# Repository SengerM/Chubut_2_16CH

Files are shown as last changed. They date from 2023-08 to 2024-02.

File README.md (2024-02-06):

# Chubut 2 16 channels

This repository contains source files of the *Chubut 2 16 channel readout board*. This board was designed to facilitate multi-channel readout of LGAD silicon sensors, such as TI-LGAD, AC-LGAD, etc. More information in [this link](https://sengerm.github.io/Chubut_2_16CH/doc/230810_characterization/main.html).

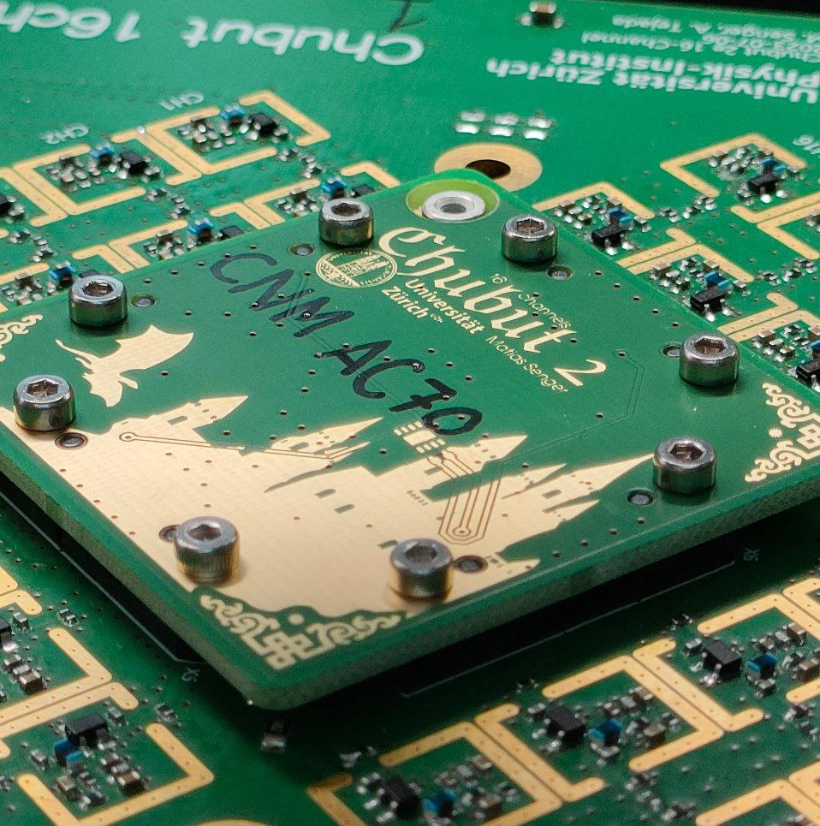
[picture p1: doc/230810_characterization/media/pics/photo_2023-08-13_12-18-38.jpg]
Picture of the Chubut 2 16ch board


Time resolution measured with a 90Sr source

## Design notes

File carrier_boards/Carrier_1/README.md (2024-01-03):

# Carrier 1

This is a general purpose carrier board for the Chubut 2 16ch readout board and can host sensors up to 3×3 mm².

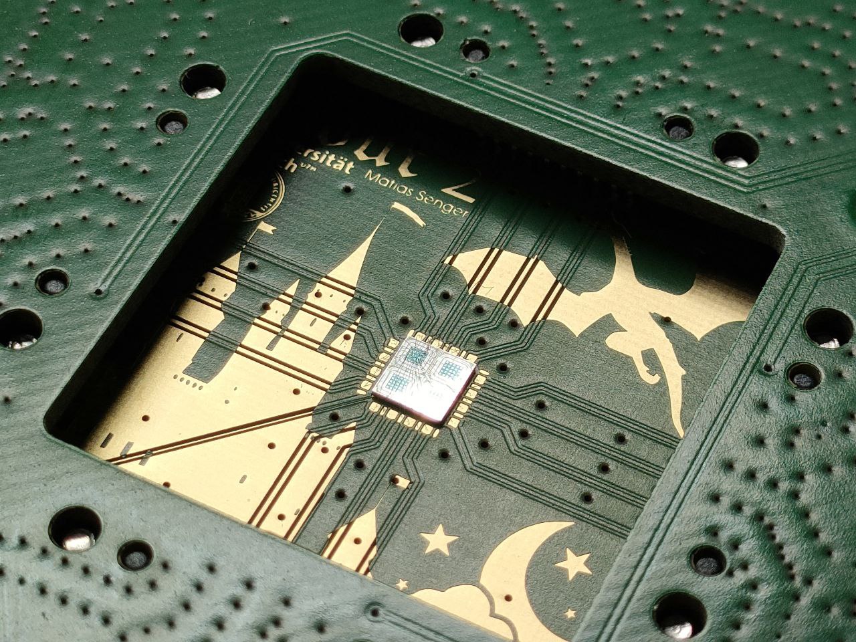
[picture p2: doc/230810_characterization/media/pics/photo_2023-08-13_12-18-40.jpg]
A picture of the Carrier 1 board


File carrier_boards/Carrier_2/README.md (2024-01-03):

# Carrier 2

This carrier board was specifically designed to host AC-LGADs manufactured by FBK, which are usually diced in groups of 3 and do not fit in other boards.

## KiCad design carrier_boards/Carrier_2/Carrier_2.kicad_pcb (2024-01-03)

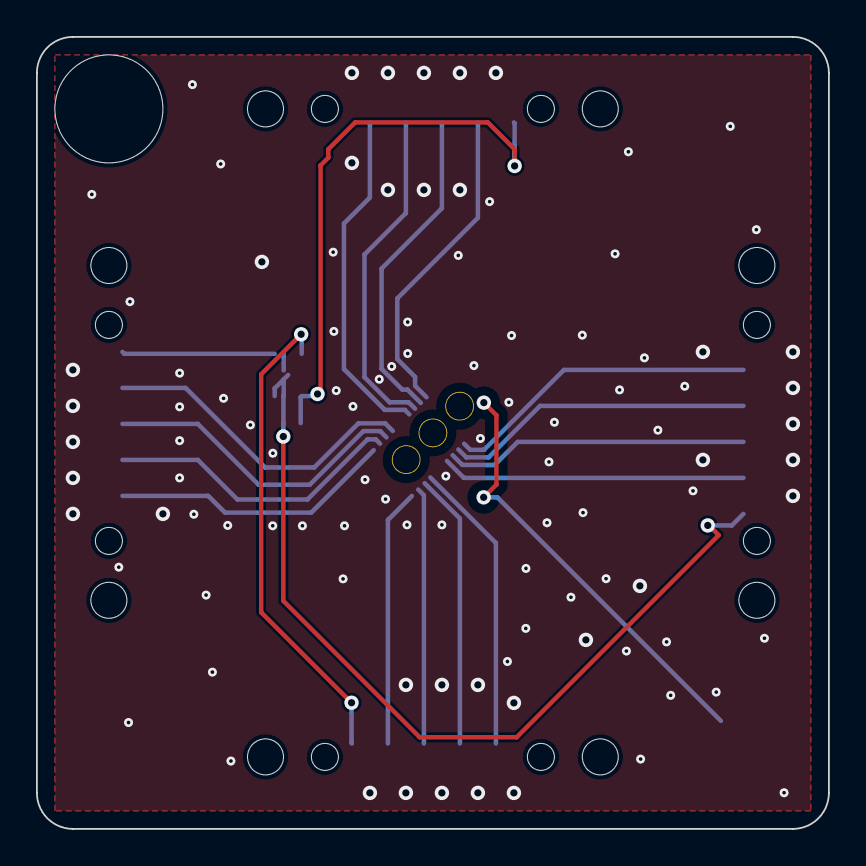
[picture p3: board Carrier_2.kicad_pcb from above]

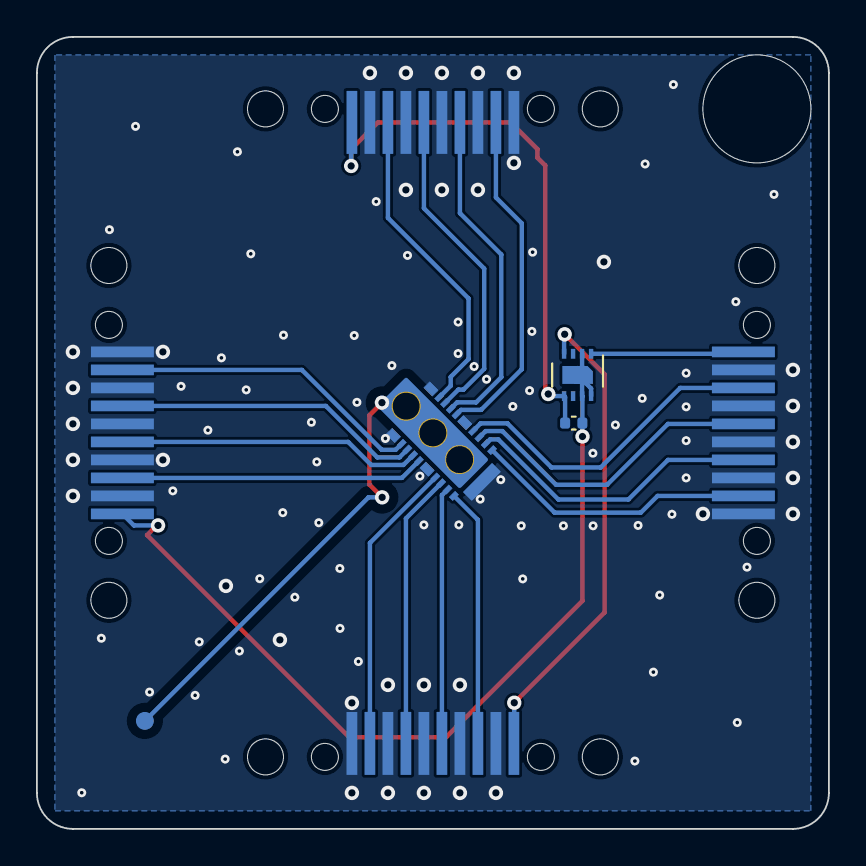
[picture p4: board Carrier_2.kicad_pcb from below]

Board: 2 copper layers, 44.0 x 44.0 mm, 9 parts (8 on the bottom side), 22 nets.

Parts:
C1: 100n; C_0402_1005Metric
H1: MountingHole; alignment_hole
J5: HV; pogo_pin_mating_pad
U1: FBK_RSD2_3_DUTs_together
U2: SHT30-DIS; Sensirion_DFN-8-1EP_2.5x2.5mm_P0.5mm_EP1.1x1.7mm
X4, X5, X6, X7: FSI-110-03-G-S-M-AD

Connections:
/HV: J5.1, U1.17 (HV)
/I2C_GND: C1.2, U2.2 (ADDR), U2.7 (R), U2.8 (VSS), U2.9 (VSS), X6.10
/I2C_POWER: C1.1, U2.5 (VDD), X7.10
/SCL: U2.4 (SCL), X5.10
/SDA: U2.1 (SDA), X4.10
GND: U1.18 (GND), X4.1, X4.3, X4.5, X4.7, X4.9, X5.1, X5.3, X5.5, X5.7, X5.9, X6.1, X6.3, X6.5, X6.7, X6.9, X7.1, X7.3, X7.5, X7.7, X7.9
unnamed: U1.1 (0,0), X4.2
unnamed: U1.15 (0,1), X5.6
unnamed: U1.14 (0,2), X5.4
unnamed: U1.12 (0,3), X6.8
unnamed: U1.2 (1,0), X4.4
unnamed: U1.16 (1,1), X5.8
unnamed: U1.13 (1,2), X5.2
unnamed: U1.11 (1,3), X6.6
unnamed: U1.3 (2,0), X4.6
unnamed: U1.5 (2,1), X7.2
unnamed: U1.7 (2,2), X7.6
unnamed: U1.10 (2,3), X6.4
unnamed: U1.4 (3,0), X4.8
unnamed: U1.6 (3,1), X7.4
unnamed: U1.8 (3,2), X7.8
unnamed: U1.9 (3,3), X6.2

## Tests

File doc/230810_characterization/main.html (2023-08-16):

Matías Senger

August 2023

This document presents the Chubut 2 16ch board, which is a version of the Chubut 2 board (https://github.com/SengerM/Chubut_2) but with 16 channels instead of 4. The board is introduced, as well as a characterization using a radioactive beta source.

## Contents

# Introduction

The Chubut 2 16ch readout board is a readout board designed for testing LGAD devices. It has 16 independent channels with built in amplification for each channel. The circuitry for each channel is replicated from the original Chubut 2 . Each channel has 2 amplification stages, making it possible to measure LGADs without the need for external amplifiers. A scheme of the board is shown in . It consists of two boards, one is the main board which contains the electronics, shown in the left of , and the other is the carrier board which only hosts the DUT, shown in the right of . The advantage of this design with a main and a carrier board is that the main board can be utilized multiple times to measure different DUTs, reducing monetary cost and work load. The carrier board fits only in one position, so it is not possible to install it wrong, and is held in place using screws. This can be seen in the pictures sown in .

 Schematic diagram of the Chubut 2 16ch readout board.

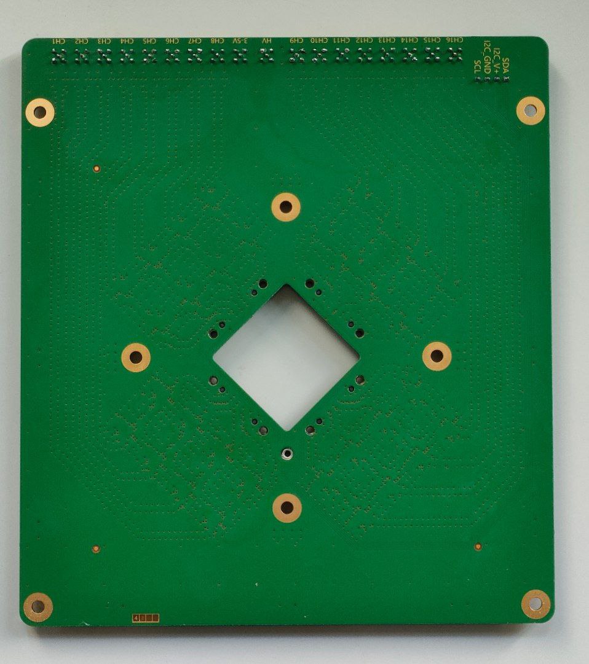
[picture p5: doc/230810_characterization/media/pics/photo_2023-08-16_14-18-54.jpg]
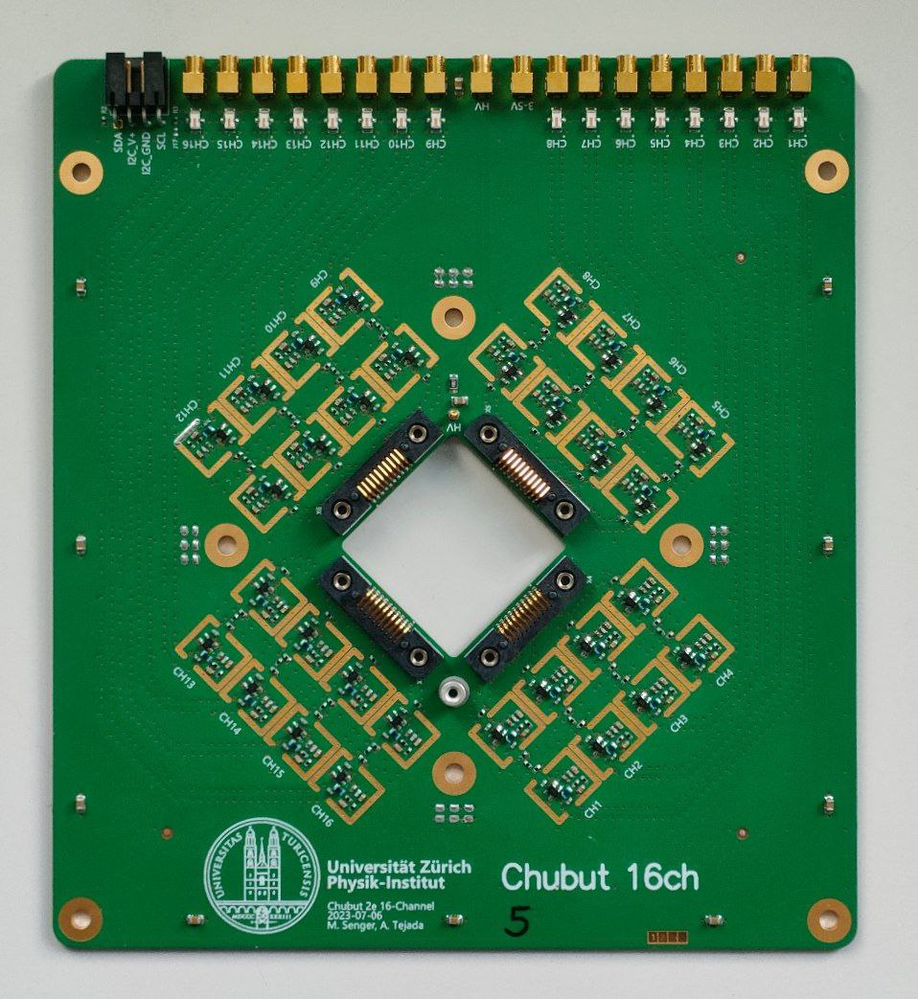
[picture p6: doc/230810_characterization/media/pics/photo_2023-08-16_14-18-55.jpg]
   

Pictures of the Chubut 2 16ch readout board.

In the following sections, more details of the board are presented.

# Temperature raise

Due to the Chubut 2 16ch readout board having 16 channels, each with two amplification stages, a considerable amount of power is dissipated. When operated at 3 V the total current drained is 700-800 mA, which means a total power of 2-2.5 W. Close to the area where the amplifiers are located, there is power dissipation and thus the temperature increases. In order to examine how much the temperature increases, pictures with a thermal camera were taken. These pictures are shown in . When these pictures were taken, the board was installed in our TCT setup. The ambient temperature, as seen in the photos, was 20 ℃. The area close to the amplifiers was approximately 12.5 ℃ higher, while the carrier board where the DUT was mounted is approximately at 27 ℃, i.e. 5 ℃ higher than ambient temperature. The carrier board is designed with the possibility of hosting a Sensirion SHT31-DIS-B (https://sensirion.com/products/catalog/SHT31-DIS-F) temperature and humidity sensor, so the temperature can be monitored.

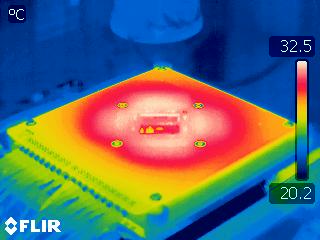
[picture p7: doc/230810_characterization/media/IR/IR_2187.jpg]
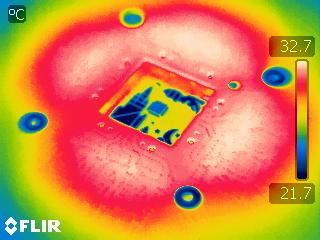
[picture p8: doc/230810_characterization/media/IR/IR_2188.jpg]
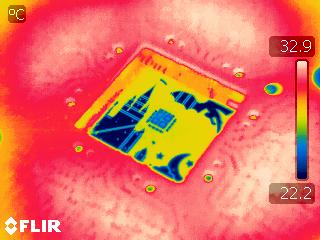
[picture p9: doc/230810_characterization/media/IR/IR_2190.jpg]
  

Photographs of the Chubut 2 16ch readout board during operation taken with a thermal camera.

# Characterization with beta source

To characterize the readout board, a TI-LGAD was mounted and exposed to radiation from a ⁹⁰Sr beta source. In a schematic representation of the measuring setup is shown. The TI-LGAD used is from the RD50 FBK production, wafer 16, 2 trenches, pixel border V2 and contact type ring. This device has a 4×4 layout with a pitch of 250 µm. The 16 pixels from the DUT were connected to each output of the readout board. The measurement was performed at +20 ℃, because the board is intended to be used in the test beam setup, probably at room temperature. The signals from the outputs of the readout board, as well as the trigger signal from the MCP-PMT, were digitized using a CAEN DT5742 digitizer, as shown in the diagram.

 Diagram of the arrangement and connections for the beta source testing.

The first check was to verify the integrity of the digitized waveforms. In example waveforms from a random event are shown. The first plot shows the raw data as provided by the digitizer. We see that channel 2 (signal_name DUT_2) has a negative peak, consistent with the expected polarity given the type of DUT, and the two channels called MCP_PMT_1 and MCP_PMT_2 have a positive peak, consistent with the expected polarity for the MCP-PMT followed by an inverting amplifying stage. The reason there are two waveforms corresponding to the MCP-PMT is due to technical details regarding the implementation of the digitizer; the 16 channels are split in two groups of 8 channels each, and each of these groups has an independent trigger signal which comes from an internal splitting of the TR0 input . For the channel 2 (DUT_2), which is the one that was hit by the beta particle in this example event, the corresponding MCP_PMT_1 is the correct trigger signal to use when calculating time quantities. In the same figure (, scroll to the right), two additional plots are shown with details of how each of the two relevant waveforms from this example are processed by the analysis algorithms. By zooming in, it can be seen that the analysis software performs a linear interpolation of the waveforms.

Waveforms from a particular event, as an example. In the first plot, the raw data from the digitizer is shown. The second and third plot (scroll horizontally) show how the relevant waveforms from the DUT and the MCP-PMT were processed.

Similar waveforms as the ones shown in are observed for all the channels. To get a first impression of how things work, it is useful to produce for all the individual waveforms a scatter plot in which the x axis is the time of the peak as measured from the trigger and the y axis is the amplitude of the signal. Such plot is shown in for a subset of the eventsThe reason for showing only a random subset of events is because otherwise the number of points in the plot is overwhelming and it becomes too heavy to load., without applying any filter. The x axis shows the quantity t_50 - t_50_trigger which is a measure of the peak time with respect to the trigger time. The quantity t_50 is the time at which the peak goes over its 50 %, as shown in the two right plots of , while t_50_trigger is the same quantity but for the corresponding MCP_PMT_1 or MCP_PMT_2 depending on the trigger group at which the channel belongs to, as described previously. In this figure we see that the majority of events distribute randomly in time and with amplitudes of approximately ±2 mV (zoom in vertically to see), which corresponds to waveforms without signal from a beta particle. There is another component in this distribution for which the time (x axis) is well localized, between ±1 ns (zoom in horizontally to see better) and negative amplitudes ranging from -40 mV and larger. These points represent the signals in each pixel of the DUT. The points corresponding to the two signals of the MCP-PMT are all perfectly aligned at t=0, the reason is that these signals are themselves the triggers, so the time with respect to the trigger is, by definition, 0.

Scatter plot of waveform amplitude vs time from trigger defined as the time from the waveform crossing the 50 % and the trigger crossing the 50 %.

To proceed further with the analysis, a threshold in the amplitude is imposed to all the DUT signals to select only those events in which the channels have an amplitude of 40 mV or larger in absolute value. In this way, all the empty waveforms are removed. shows the distribution of amplitudes after performing the selection of events. The plot on the left shows the empirical cumulative distribution function (ECDF) and the plot on the right (scroll horizontally) shows a histogram and a langauss fit (Landau convoluted with Gaussian) to each channel. In this last plot, the traces can be enabled for the channels not shown by clicking on the elements in the legend, only channels 1 and 2 are shown by default for the sake of clarity.

Amplitude distribution after selecting those waveforms with an amplitude larger than 40 mV in absolute value. In these plots, the quantity shown is the amplitude multiplied by -1 to make it positive. The first plot shows the empirical cumulative distribution function (ECDF) and the second plot shows the histograms together with a langauss fit (Landau convoluted with a Gaussian). To enable/disable traces, click on the elements in the legend.

In the distribution for other parameters, after applying the cuts in the amplitude, are shown (scroll horizontally if needed to see all of them). As seen, the signal to noise ratio has a median that oscillates between 120 and 135, for the rise time the median oscillates between 980 and 1010 ps, the median noise is between 610 and 660 µV, the median pulse duration above 50 % threshold is between 1.42 and 1.48 ns and the integral under the peak, called Collected charge (V s) in the plot, has a median between 115 and 138 ×10⁻¹² V s. All these quantities are calculated individually for each waveform as shown in the two example plots to the right in . From all these distributions, and the ones shown in , it can be concluded that the system is performing properly and the response of each channel is uniform.

Other distributions obtained in the same conditions as for the ones shown in , i.e. after selecting the events by amplitude. The quantities shown in these plots correspond to the parameters shown in the analyzed waveforms to the right in . Scroll horizontally to see all of them.

Among the most important parameters to be determined using the readout board is the time resolution of the DUT. To calculate the time resolution, or, firstly, the jitterHere, jitter is understood as the fluctuations in the time at which a signal crosses some threshold, see this image (https://upload.wikimedia.org/wikipedia/commons/thumb/8/8d/Jitter_timing.svg/660px-Jitter_timing.svg.png) taken from the Wikipeida article on jitter (https://de.wikipedia.org/wiki/Jitter)., the time information from each peak is extracted. This information conists on a set of 9 parameters extracted from each peak, labeled t_10, t_20, ..., t_90 that measure the time at which the peak went above the corresponding percentage of its own amplitude, i.e. applying a constant fraction discrimination, as shown in the two plots on the right in . Having these values, then it is possible to select any pair of signals, say DUT_1 and MCP_PMT_1, and calculate the time difference for some pair of kCFD values, say 20 % and 20 %. This means to compute Δt = t_20DUT_1 - t_20MCP_PMT_1 for each event. An example is shown in . The fluctuations observed in Δt correspond to the jitter for this particular choice of signals and thresholds, i.e. the fluctuation in the time for which one of the signals crosses some threshold, regarding the other as the time reference.

Example of Δt distribution for kCFD, DUT_4=40 % and kCFD, MCP_PMT_1=50 %, together with a Gaussan fit.

The pairs of signals for which the jitter is relevant are each of the DUT channels and the corresponding trigger signal according to the trigger group, as detailed previously, which is coming from the MCP-PMT time reference. The values for the kCFD thresholds have to be chosen according to some criterion. Two common choices are either to fix them at 20 % or to keep them free and choose those which minimize the jitter. In the jitter for each channel is shown; the plot in the left has kCFD optimized while the plot in the right has kCFD fixed at 50 % for each signal. It can be seen that the results are more uniform for the optimal case, yielding an average value of ~42 ps of jitter while for the right plot with kCFD fixed we obtain an average value of ~48 ps.

Jitter obtained for each readout channel and the corresponding MCP_PMT_x signal. The plot on the left shows the reuslt when the kCFD is chosen to obtain the optimal result, the plot on the right (scroll horizontally if needed) shows the result when the kCFD is kept fixed at 50 % for each signal.

To ultimately obtain the time resolution of the DUT from the data shown in , the contribution from the MCP-PMT has to be subtracted in quadrature to the jitter. This requires a prior calibration of the MCP-PMT, together with the amplifier that is being used, the digitizer, as well as the particular trigger threshold and kCFD value. This exercise was not performed so the right value is unknown, but it is expected to be in the range between 15-25 ps . However, the jitter values obtained in are compatible with values obtained in the past using similar DUTs but different readout boards (Santa Cruz board) and different digitizers (LeCroy 4 GHz, 40 GS/s oscilloscope) which oscillate between 35 and 40 ps. It has to be taken into account that these values were obtained measuring at -20 ℃, while the current study was performed at +20 ℃. Considering a contribution from the MCP-PMT signal of 20 ps, then the time resolution for each channel oscillates between 37 and 43.5 ps, which is reasonable and expected.

# Conclusions

A new readout board for pixelated LGADs was designed, implemented and tested in laboratory conditions. The board has 16 readout channels, each with two amplification stages thus eliminating the need for external amplifiers. The design includes the splitting of the readout board into a main board and a carrier board which makes it very convenient to test multiple devices and reducing both monetary and work-load costs.

The characterization with beta source shows that the response of all the 16 channels of the board is uniform and performs as needed to make time resolution studies. The board is also compatible with the CAEN DT5742 digitizer.

# References

CAEN DT5742 user manual. https://www.caen.it/products/dt5742/. Determining the time resolution of the Photonis MCP-PMT with betas. https://sengerm.github.io/html-github-hosting/220126_Photonis_PMT_time_resolution/index.html. Effect of bandwidth in time resolution CAEN digitizer vs LeCroy oscilloscope, presented in AIDAInnova WP6 Test beam preparation #3. https://indico.cern.ch/event/1279942/contributions/5378119/attachments/2648690/4585355/bandwidth_studies.pdf. Chubut 2 repository. https://github.com/SengerM/Chubut_2.

# Footnotes

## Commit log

2023-08-16 Added temperature information and some pics
2023-08-16 Added info about temperature sensor
2023-12-07 New version, DUT rotated 45 deg and slightly more space for BNL sensors
    [Carrier_1.kicad_pcb]
2024-01-03 Implemented a carrier board for the FBK AC-LGADs which are diced all together
    [Carrier_2.kicad_pcb, Carrier_2.kicad_sch]
